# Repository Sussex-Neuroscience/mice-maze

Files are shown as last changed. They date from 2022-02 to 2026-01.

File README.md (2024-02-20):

# Mice maze
#### Active exploration setup for rodents

This is a repository for building and running an experiment investigating how sensory cues affect mouse exploration in a modifiable maze.

### List of repository contents ###

#### 3dmodels
* Models used to make/3dprint parts used in the maze setup.
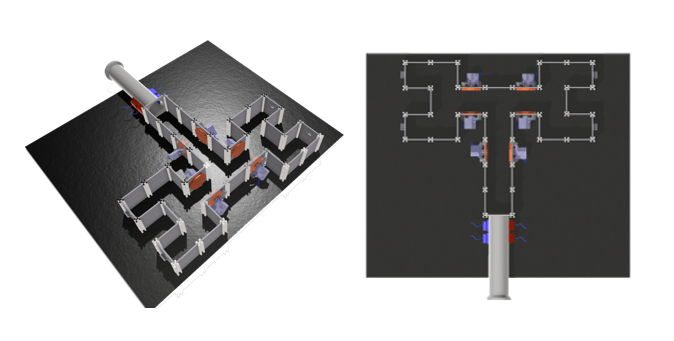
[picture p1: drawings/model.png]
alt text for screen readers tunnable walls


#### code
* Contains code used in the project.
* * Scripts used to process the video recordings of mice in the maze and a script used for the pilot deeplabcut test.
* * Arduino code to control stimuli settings and reward delivery.
* * Walkthrough to use the automatic maze.

#### construction_photos
* A selection of photos of the maze during it's development for illustrative purposes.

#### drawings
* Schematics and drawings. Such as the format of the base plate holes.

#### Contributors of the maze:
* Miguel Maravall
* Oluwaseyi Jesusanmi
* Andre Maia Chagas
* Yuri Elias Rodrigues
* Maja Nowak
* Marcus Burnell-Spector
* Shahd Al Balushi
* Isabel Maranhao
* Alejandra Carriero

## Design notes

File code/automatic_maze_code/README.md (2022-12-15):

## Automatic maze code

#### Entry sensor code using Beehive+micropython - **sensor.py**
* write on the terminal (Linux) when instructed
```
ampy --port /dev/ttyUSB0 --baud 115200 run path_to/sensor.py &> sensor.csv
```

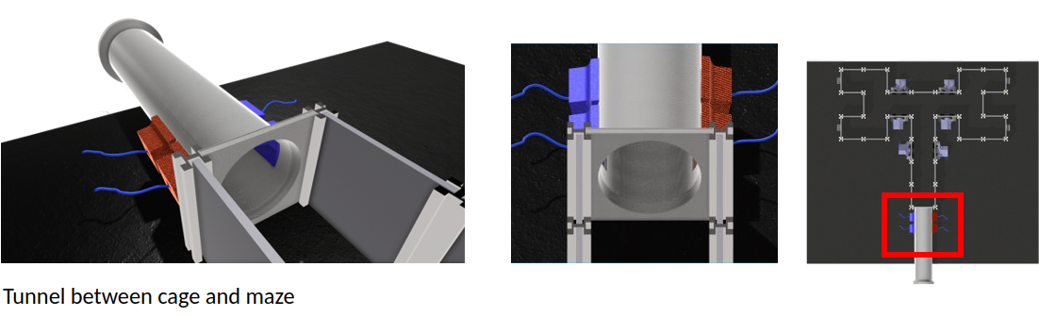
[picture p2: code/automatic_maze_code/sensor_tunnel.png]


#### Grated tunable walls code - *tunable_walls.py*
* First, upload a *standard firmata* ([tutorial how to upload standard firmata](https://www.instructables.com/Arduino-Installing-Standard-Firmata/)) to an Arduino Uno, and wire it using a breadboard.
* A calibration file needs to be created to interpolate the angles measured at 0°, 45°, 90° and 135°. A calibration example sheet is given at **angle_tuning.csv**.
* Once the servos are calibrated, the angles can be defined as the function *move_servo_tuned()* at *tunable_walls.py*. Example:
* * Move servo labelled "RR" to 90 using:
```
move_servo_tuned(90,"RR")
```

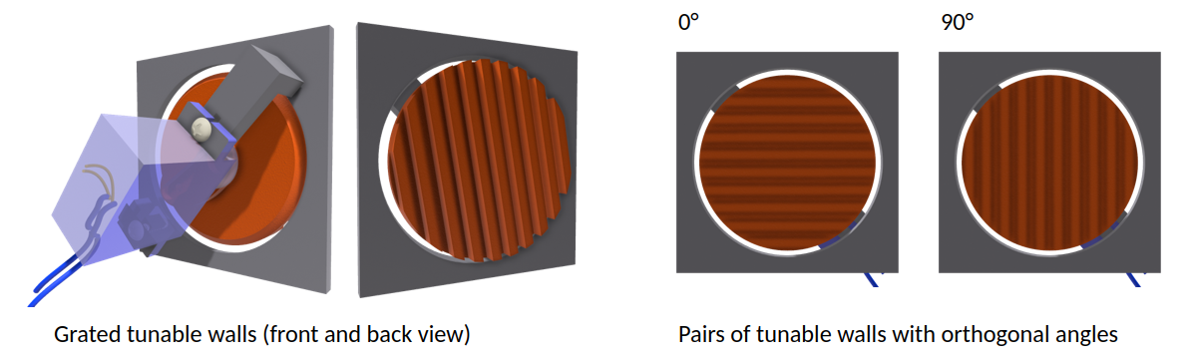
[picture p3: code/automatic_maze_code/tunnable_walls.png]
alt text for screen readers tunnable walls


#### Food delivery - *food_delivery.py*
* Food delivery is similar to the tunable walls code. First, upload *standard firmata* to an Arduino Uno and wire it using a breadboard.
* A calibration file also needs to be created to match the order in which the food pellet will be delivered and the necessary rotation. An example of the calibration is given at *food_tuning.csv*. The tunning can be found using the function *move_food_order()*. For example, a way to slowly deliver the reward:

```
for i in range(0,23,2):
      time.sleep(0.1)
      move_food_order(i,'LR')
```

#### Camera and position tracking for automated reward delivery - *automatic_maze_code_with_food.py*
* All operations on the camera are done using cv2-python. The detection of a correct trial is triggered using a pixel intensity threshold against a background recording done before the cage is placed. Note that the maze should not be shaken during this operation to displace the region of interest where the pixel intensity is measured.
* Sensor plotting is done in real-time using [PyQtGraph](https://www.pythonguis.com/tutorials/plotting-pyqtgraph/) for efficiency.
* Routines depending on the camera:
* * Pixel intensity averages for trial definition (hit/miss)
* * Position detection.
* * Time spent by the mouse in each region by trial and by session (*only implemented for the reward delivery place*).
* * Gimbal camera and focus feedback (*to be implemented*).
* * Distance/speed measures along the trial and session (*to be implemented*). This can be used to measure the engagement and how fast the mice finish the trial.
* * Tunable wall proximity measure (*to be implemented*). This would be useful to measure

#### GUI

#### Analysis code (to be implemented)
* Summary and update results to the last results
* Update a Markov model to predict exploration patterns using time spent on a region of interest covering the whole maze (online and offline).

#### Behavior task description on the automated maze (food version)
#### Behavior task description on the automated maze (liquid version)

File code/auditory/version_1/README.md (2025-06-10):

# Welcome to the Auditory part of the maze
## Hope you're here to stay!!

- The main logic of the experiment is in `main.py`. Feel free to modify it according to your needs. The code is designed to ask for user input but it is optimised to let you just hard code variables instead (it gets annoying to always input the same values for different mice, I get it. But if you work on more dynamic experiments, you have the option. All in all. The setup is designed to **give you options, nothing but options**.) 

- The trials generation is handled in `supfun_sequences.py`. 

- If you haven't calibrated your speaker yet, what are you waiting for? Head over to `speaker calibration scripts`. 
- If you don't need speaker calibration / have a better method (rude, but fine. At least share. How did you do it?), I recommend running `calibration_volume.py` to check which channel the sounds come out of.

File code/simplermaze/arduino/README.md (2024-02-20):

the code to run the servos requires an adafruit library as well as a serial communication parsing library. they can be found:

- https://github.com/adafruit/Adafruit-PWM-Servo-Driver-Library
- https://github.com/kroimon/Arduino-SerialCommand

more info on how to use the adafruit library here: 
https://learn.adafruit.com/16-channel-pwm-servo-driver/using-the-adafruit-library

Serial commands are structured in the following way:

- to change the orientation of a grating, the command going to the arduino board should be a string with the keyword "grating", followed by the coded location of the grating and the angle the grating needs to be moved to. Example: "gratingLL 180"

- to send commands for rewards to be dispensed, the command going to the arduino board should be a string with the keyword "reward", folllowed by the location where the reward is to be given. Example: "rewardA"

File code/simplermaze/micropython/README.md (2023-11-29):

## code to run the PCA9685 on micropython

this leverages the Adafruit library which is currently not being actively developed.

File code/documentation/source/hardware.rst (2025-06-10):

Hardware Documentation
======================

Materials List
--------------

General Materials
-----------------
- **Panels and Baseplate**:
  - 50 side panels: Black, 50 × 50 × 3 mm.
  - 1 baseplate: 10 mm thickness, 700 × 700 mm, black infrared-transmitting (Code: 962).
- **Maker Beams for Structural Support**:
  - XL beams (50 mm length, black anodized aluminum).
  - **Bolts for Maker Beams:** M3 bolts (16 mm), M3 nuts (1 per bolt).
- **Bolts for Feet:** M6 bolts and nuts for stabilization (1 per corner).
- **Legs:**
  - Dimensions: 50.8 × 50.8 × 1.6 mm.
  - Length: 880 mm; horizontal bars: 660 mm.
  - Accessories: 4 plastic joints and bottoms.

Construction Instructions
-------------------------

Base Assembly
~~~~~~~~~~~~~
1. Attach the maker beams to the baseplate using M3 bolts and nuts.
2. Ensure a stable connection by tightening each bolt securely.

Legs and Stabilization
~~~~~~~~~~~~~~~~~~~~~~
1. Secure the legs to the baseplate using M6 bolts and nuts.
2. Add plastic joints and bottoms for stability.
3. Verify the assembly is level to prevent wobbling.

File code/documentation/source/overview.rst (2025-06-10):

Overview
========

The Mice-Maze project provides a modular system for researchers to investigate rodent exploration behavior and sensory cue processing. The maze's flexible design includes interchangeable components and precise control of environmental stimuli. This documentation details the hardware and software requirements, assembly instructions, and usage guidelines.

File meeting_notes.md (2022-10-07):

### Meetings:

#### 19/01/2022 Seyi & Andre
Figuring out initial bill of materials and acrylic dimensions:

- considerting the use of makerbeams (plates will slide in them), we need acrylic plates that are a bit longer than the area the mouse will have access to.

All side/wall plates will have the same dimensions and there will be a base plate and a ceiling plate.

on the base plate we will have regularly spaced threads, so that makerbeam posts can be fixed in. and different maze styles can be built.

- base plate: (paper dimensions - 12.7mm thickness 609.6 X 609.6 mm) for our system: 600 X 600 X 12 mm
- side plate: (paper dimensions - 40.63 X 50.8 X 3.175 mm) For our system: 50 X 50 X 3 mm 
- maker beams XL for support: 50mm length, black anodised aluminium.
- M3 bolts to fix the makerbeams on the plates
- m6 bolts as feet for the floor plate

local company for acrylic: https://www.brightonandhoveplastics.co.uk/index.php/products-acrylic_sheet/?k=23991:5::
makerbeam shop https://www.makerbeam.com/makerbeamxl/makerbeamxl-15x15mm-profile-lengths-anodised-in-bl/
screwfix for bolts https://www.screwfix.com/p/easyfix-bright-zinc-plated-pan-head-machine-screws-m3-x-20mm-25-pack/5875j?cm_sp=managedredirect-_-screwsfixings-_-m3bolts&_requestid=183859

We decided to go for an 4 arm maze initially to test things.

There are 8 end points in this. 

To build this, we need (with spares) 50 side panels and 50 makerbeam posts, celing and floor plates.
Also need M3 bolts

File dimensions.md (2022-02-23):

***Converted/ extracted dimensions of Rosenberg Maze***

Whole maze dimensions Length: 609.6mm, Width: 609.6mm, Height (ie Floor to ceiling): 50.8mm

Ceiling thickness: 12.7mm
Acrylic wall thickness: 3.175mm

Corridor width: 28.575mm

In their design. From the top of the maze to the bottom there are 15 panels. 609.5/15=40.63

Therefore each panel width is 40.63mm

To the first junction (the first T) there are 7 panels. So the first corridor is 284.41mm.

Turning into the arms of the T there are 3 panels on each side, meaning an arm length of 121.89

***Measurements for our project maze***

Makerbeams: Height and width of 10mm. Variable length. They will be above and below the acrylic wall.

Acrylic wall height: 30.79mm  
Acrylic wall panel length: 40mm  
Acrylic wall panel thickness: Dependent on makerbeam T-slot.

Maker beams have optional lengths of 40mm premade, which is close to thee 40.63mm panels of the Rosenberg made, so we can alter the panel width to suit this.

To form a T-maze only, these are the number of parts needed.  
Number of panels needed: 29  
Number of (40mm) makerbeams needed: 58

***Final part measurements used during construction***

*A few measurements to be reconfirmed with tool*

Acrylic wall panels: H-50mm, L-50mm, W/Thicness - Xmm   

Screws: M3 16mm, with an M3 nut used on the underside of the maze baseplate.

Baseplate Thickness: 10mm (Smaller thicknesses of ~7.5mm up would also work.
Baseplate is 700mm by 700mm.

Makerbeams: [10 x 10 makerbeams](https://www.makerbeam.com/makerbeam/makerbeam-10x10mm-profile-lengths-anodised-in-blac/) were used with a custom length of 50mm.

Infra-red camera used is found at [this link](https://www.amazon.co.uk/ELP-Webcam-Windows-machine-ELP-USBFHD05MT-RL36-U/dp/B015VE6MII/ref=sr_1_1_sspa?crid=1YP1F3UZ7P0DA&keywords=elp+infrared+camera&qid=1643305666&sprefix=elp+infrared+camera%2Caps%2C273&sr=8-1-spons&psc=1&spLa=ZW5jcnlwdGVkUXVhbGlmaWVyPUEyVTRNUFhHNFo2VUYwJmVuY3J5cHRlZElkPUEwNzY4NTUyMTJWRjROS0NGMTdWSiZlbmNyeXB0ZWRBZElkPUEwMjA0ODUwMkg1SVhWTzJMSVlXUyZ3aWRnZXROYW1lPXNwX2F0ZiZhY3Rpb249Y2xpY2tSZWRpcmVjdCZkb05vdExvZ0NsaWNrPXRydWU=), and the infra-red illuminator is a [this link](https://www.amazon.co.uk/dp/B01N76QRHV/ref=sspa_dk_detail_1?psc=1&pd_rd_i=B01N76QRHV&pd_rd_w=BuWW7&pf_rd_p=c899a50b-8835-46b4-89a0-fdf052ea9b60&pd_rd_wg=3Z9Ro&pf_rd_r=JVWXG686S572C72FK036&pd_rd_r=87af8edc-d196-40cb-8f1a-5166b4e7a4cc&spLa=ZW5jcnlwdGVkUXVhbGlmaWVyPUEyV1JNU0FENUtYVzZVJmVuY3J5cHRlZElkPUEwNDI2ODEyRFlDRFlOTjgwSEJYJmVuY3J5cHRlZEFkSWQ9QTA2MTg4OTc0MFcySUoxOUw3OVkmd2lkZ2V0TmFtZT1zcF9kZXRhaWwmYWN0aW9uPWNsaWNrUmVkaXJlY3QmZG9Ob3RMb2dDbGljaz10cnVl)

We will use [these beams](https://www.metals4u.co.uk/materials/aluminium/aluminium-box-section/799-p?vat=inc&gcl[…]yC8SSxSnme3ri-O_1YQuGo-yPlagg_-HQaAv4HEALw_wcB&gclsrc=aw.ds) for the frame, with velcro on the maze baseplate and and on the beams for easy removal.
The beams fit together with plastic joints, and from the end of a joint to where the bar fits to the joint is 40mm.
We will 4 metal bars of 620mm each to go around the outside of the maze. And 4 bars of 760mm each to be the legs of the maze.

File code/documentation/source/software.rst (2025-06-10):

Software Documentation
======================

Code Overview
-------------
- The repository includes:
  - Scripts for video processing and analysis.
  - Code to control maze stimuli and motor functions.

Running the Software
--------------------
1. Launch the Python script to initialize the experiment.
2. Adjust camera settings and stimuli parameters as needed.
3. Begin the experiment and monitor data collection.

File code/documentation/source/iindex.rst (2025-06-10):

.. Mice maze documentation master file, created by
   sphinx-quickstart on Thu Oct 10 16:22:44 2024.
   You can adapt this file completely to your liking, but it should at least
   contain the root `toctree` directive.

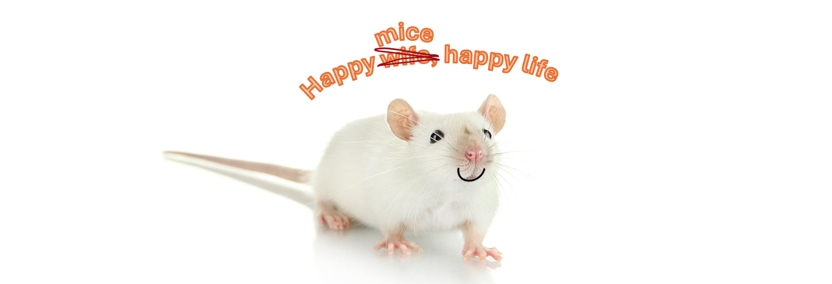
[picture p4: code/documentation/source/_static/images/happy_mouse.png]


the aMAZEing maze documentation
=======================

**Active exploration setup for rodents**
This is a repository for building and running an experiment investigating how sensory cues affect mouse exploration in a modifiable maze.

Check out the :doc:`usage` section for further information, including how to :ref:`install <getting_started>` the project.

Welcome to Mice-Maze Documentation!
====================================

.. toctree::
   :maxdepth: 2
   :caption: Contents

   overview
   getting_started
   hardware
   software
   usage
   examples
   troubleshooting
   references

Indices and tables
==================
* :ref:`genindex`
* :ref:`modindex`
* :ref:`search`

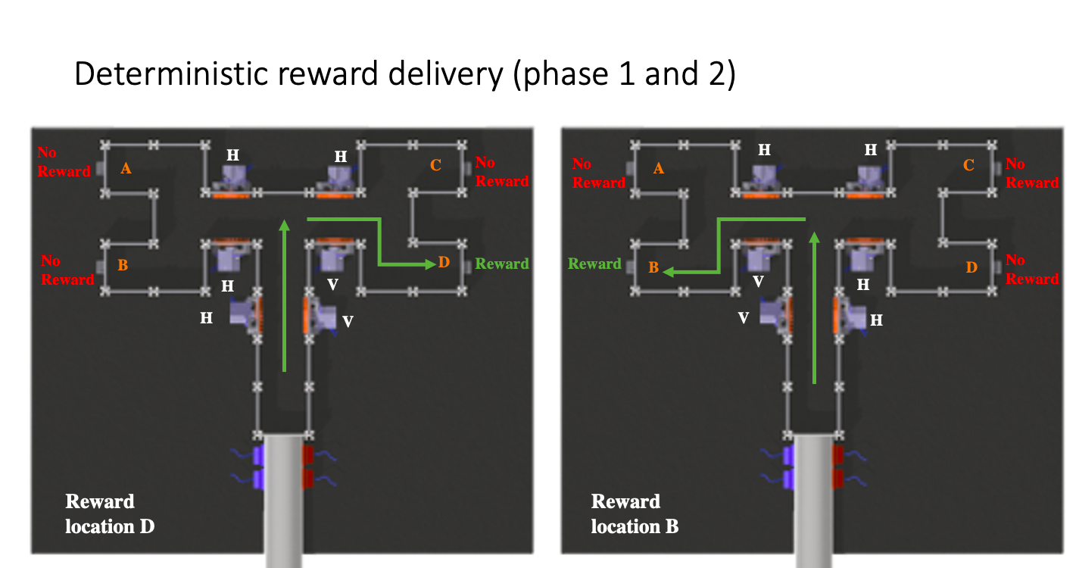
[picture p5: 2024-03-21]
drawings/task_design_2.png

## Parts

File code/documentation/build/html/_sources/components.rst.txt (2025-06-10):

Build the maze
==================

Maze structure
_______________

To build this, we need (with spares):

- **50 side panels and 50 maker beam posts, and floor plate. Also need M3 bolts, legs and camera**

- **Colour for baseplate and panels:** Colour: Black Code: 962, Dimensions(mm): 3050 x 2030, Thickness (mm): 3 – 15, Light Transmission (%): 0 Infrared Transmitting Side panels: 50 X 50 X 3 mm Baseplate: Thickness is 10mm, size 700mm by 700mm Maker beams: maker beams XL for support: 50mm length, black anodised aluminium.

- **Bolts for maker beams:** M3 bolts to fix the maker beams on the plates (M3 16mm, with an M3 nut used on the underside of the maze baseplate.) (1bolt and 1 nut per Maker beam) (bolts and nuts can be bought from screwfix?)

- **Bolts for feet:** M6 bolts as feet for the floor plate – Bolts not attached to the legs, it is to prevent the top falling off. One nut of top side and one a bottom side, with one bolt per corner. (bolts and nuts can be bought from screwfix?) Legs: 50.8mm x 50.8mm x 1.6mm, with Legs length 880mm, the bars that go round are 660 mm, 4 plastic joints and 4 plastic bottoms for the feet

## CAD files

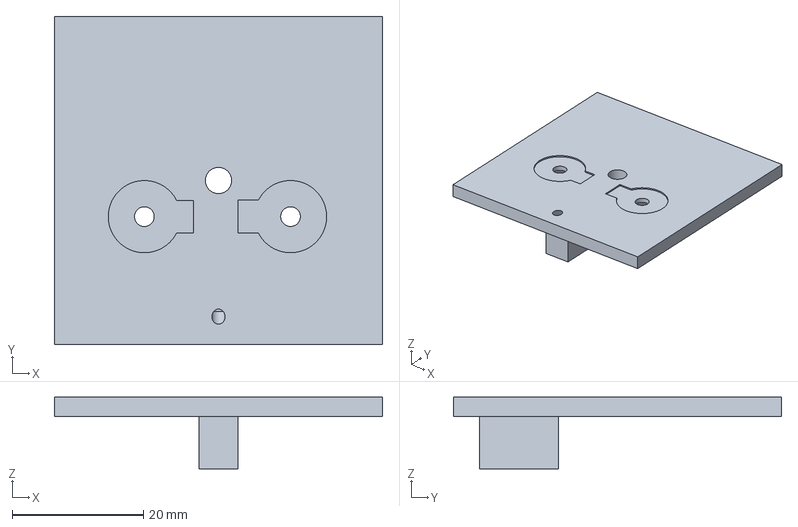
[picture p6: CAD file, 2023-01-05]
3dmodels/maze_parts/spout/spout_holder-main_plate.amf
50.0 x 50.0 x 10.9 mm

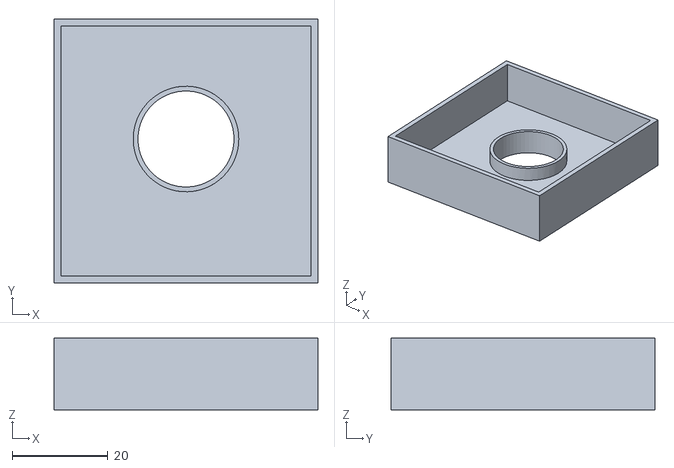
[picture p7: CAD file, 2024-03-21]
3dmodels/camera_holder/camera_lid_v1.stl
55.0 x 55.0 x 15.0

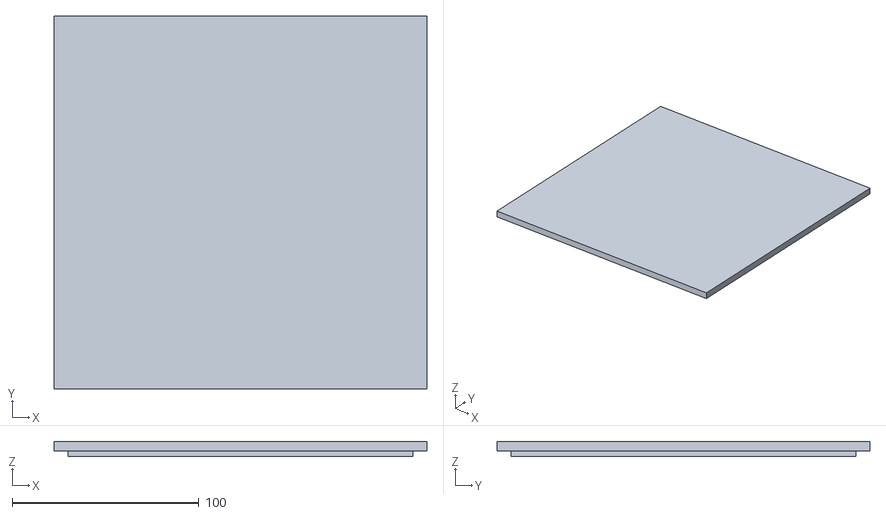
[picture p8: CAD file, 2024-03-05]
3dmodels/electronics_enclosure_lid_v2.stl
200.0 x 200.0 x 8.00

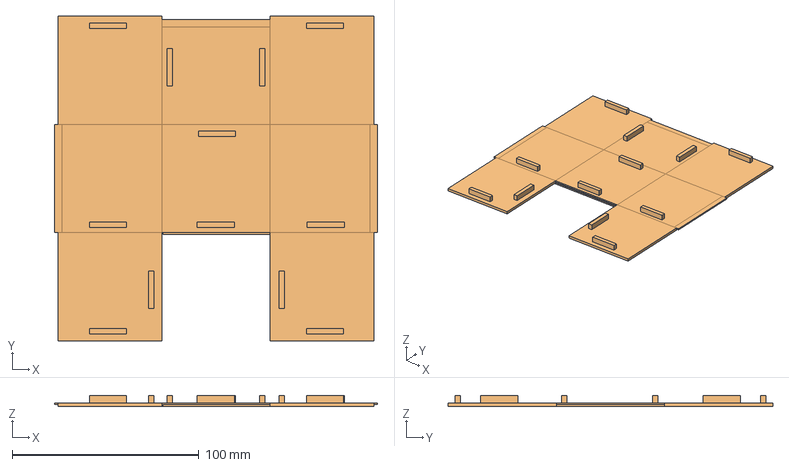
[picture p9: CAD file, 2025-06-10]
3dmodels/maze_parts/maze_cover/maze_cover_B_v4.FCStd
173.0 x 174.0 x 6.00 mm

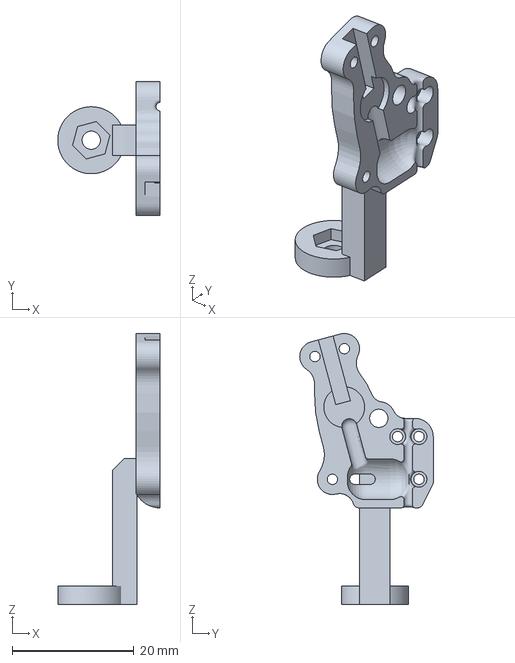
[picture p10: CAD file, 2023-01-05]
3dmodels/maze_parts/spout/spout_holder-holder_left.amf
16.8 x 21.9 x 44.5 mm

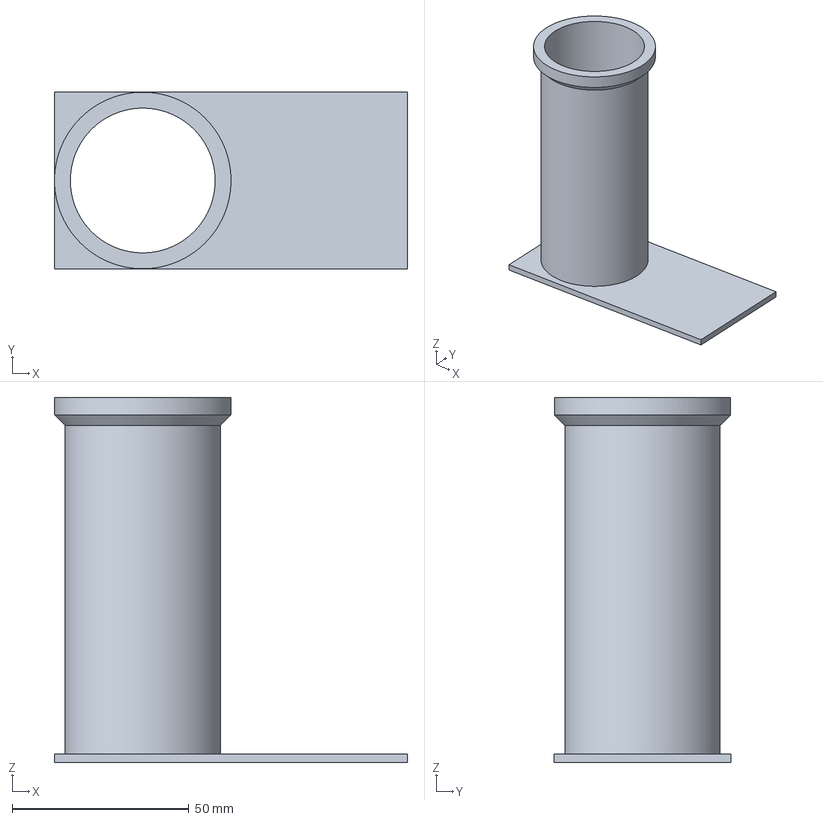
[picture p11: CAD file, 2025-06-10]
3dmodels/maze_parts/tunnel/Maze2_transfer_tunnel_higher.walls.3mf
100.0 x 50.0 x 103.5 mm

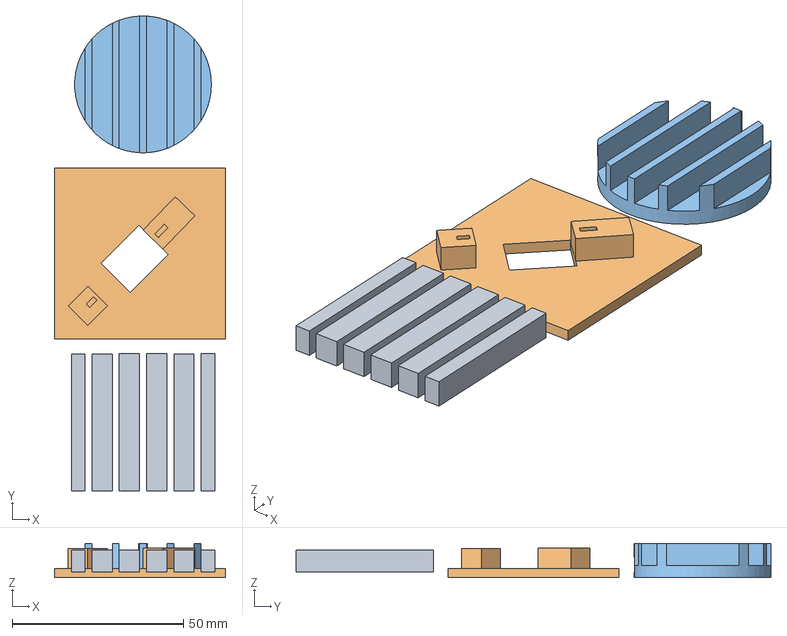
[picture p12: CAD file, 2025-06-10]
3dmodels/moveable_wall/cog calibration/new_wall_maze_v15.FCStd
50.0 x 138.9 x 10.0 mm

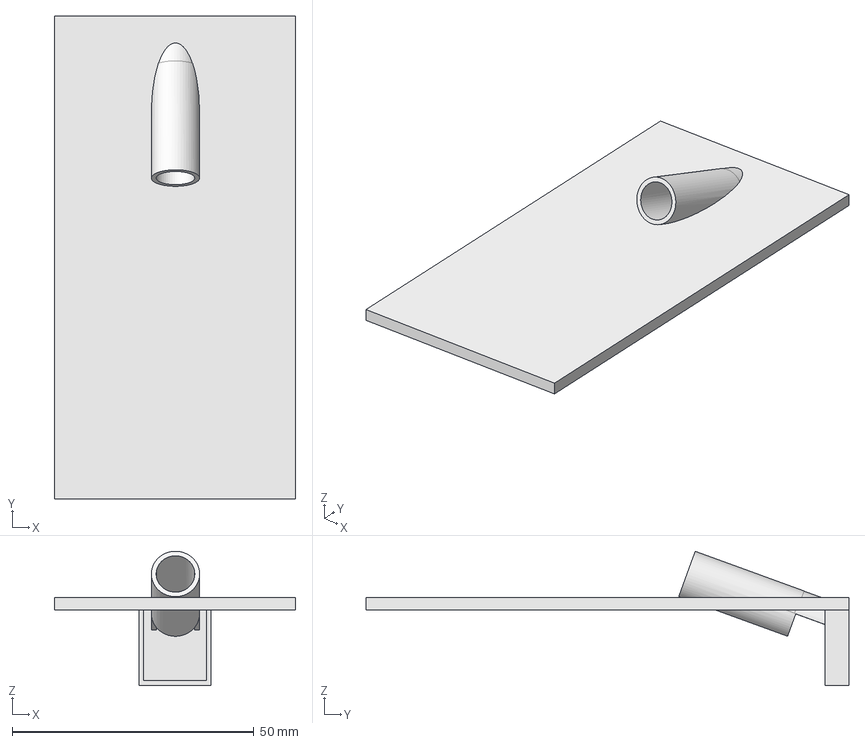
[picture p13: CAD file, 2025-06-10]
3dmodels/reward delivery/reward_chute_Wall_v4.FCStd
50.0 x 100.0 x 27.8 mm

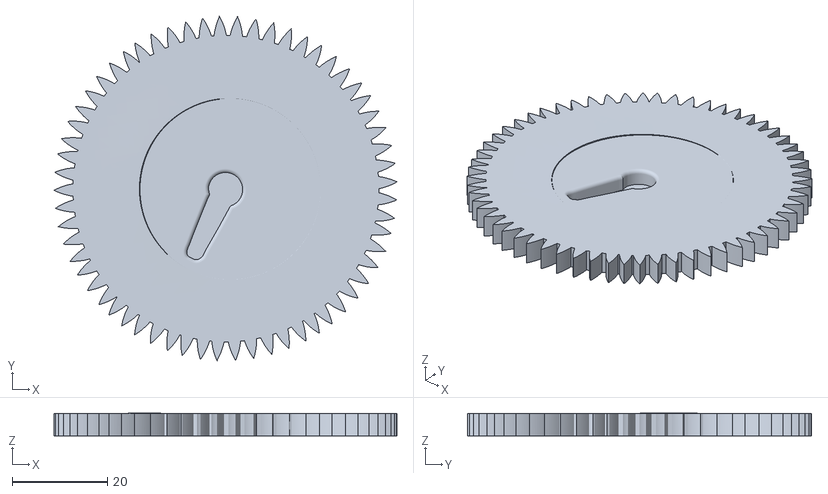
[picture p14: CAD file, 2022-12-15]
3dmodels/solid_reward_tray/cog.stl
72.1 x 72.3 x 4.78

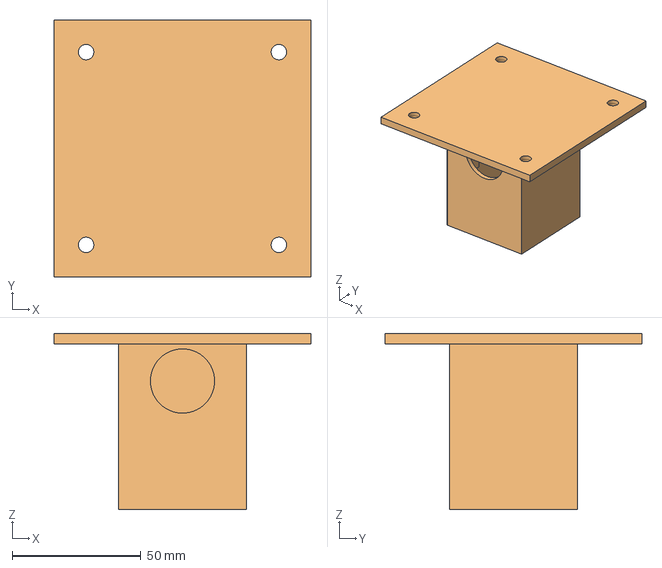
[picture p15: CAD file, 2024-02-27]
3dmodels/camera_holder/camera_box_v3.FCStd
100.0 x 100.0 x 68.5 mm

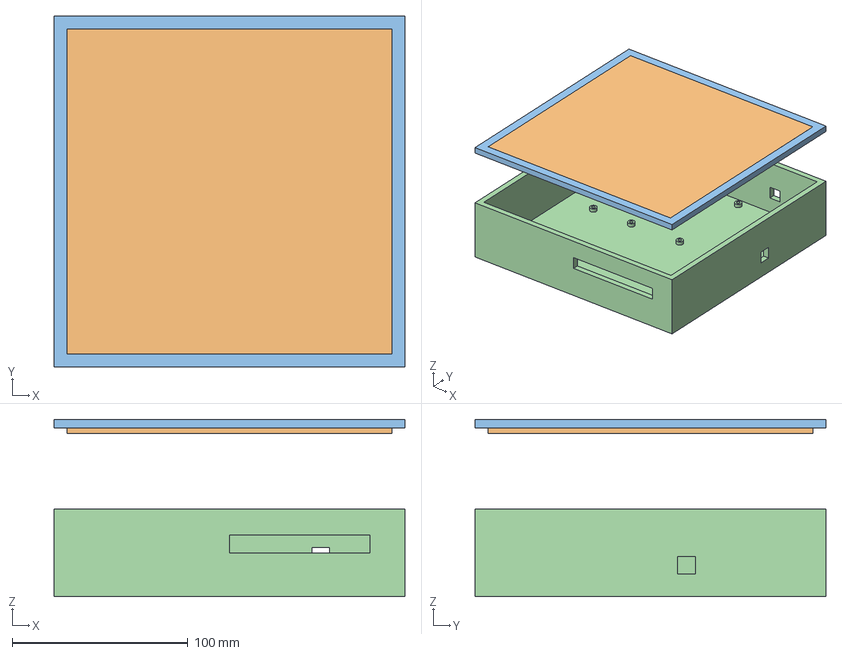
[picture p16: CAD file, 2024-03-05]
3dmodels/electronics_enclosure_v2.FCStd
200.0 x 200.0 x 101.0 mm
lid

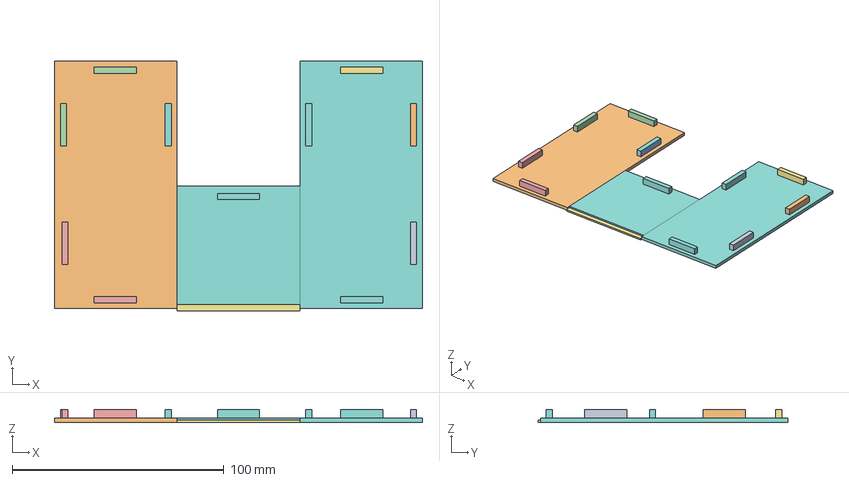
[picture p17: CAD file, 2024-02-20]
3dmodels/maze_parts/maze_cover/maze_cover_C_v3.FCStd
174.0 x 118.0 x 6.00 mm

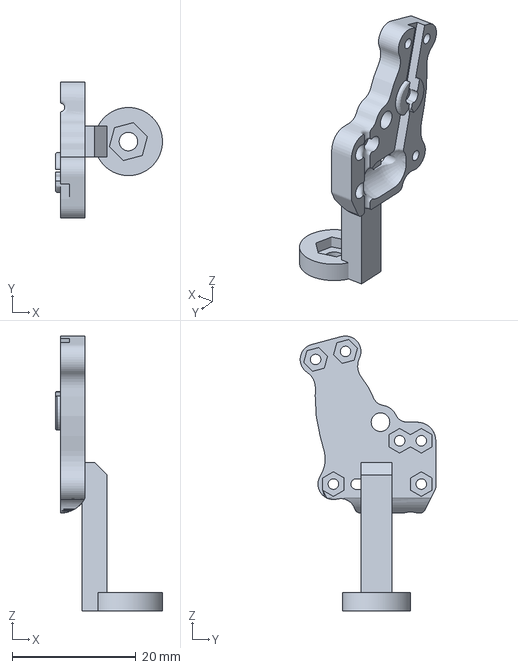
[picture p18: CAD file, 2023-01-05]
3dmodels/maze_parts/spout/spout_holder-holder_right.amf
17.3 x 21.9 x 44.4 mm

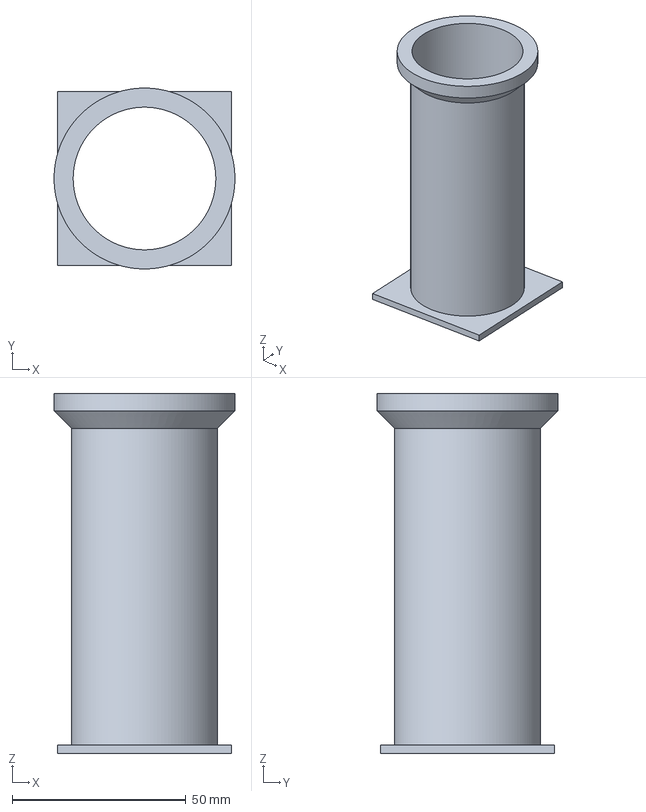
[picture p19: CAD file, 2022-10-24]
3dmodels/maze_parts/tunnel/transfer_tunnel-Cut.amf
52.0 x 52.0 x 103.5 mm

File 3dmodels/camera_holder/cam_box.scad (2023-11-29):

//cable hole diameter
cb_diameter = 20;

//base of camera board to top of lens
cam_h = 25;

//height camera should be suspended above the bottom of the box
cam_suspend_h = 30;

//side length of square indents the camera board will rest on
rest_indent_l = 7;

//whole camera board length. It is square
cam_board_l = 39;

//wall thickness of box x2
wall_thick = 6;

//length of box
box_l = cam_board_l+wall_thick;


//base square length
base_l = 70;

//added distance to get to middle of base square
base_add = (base_l-(cam_board_l+wall_thick))/2;

//subract cylinder from box with subracted box
translate([base_add, base_add, wall_thick])
{
difference()
{
// make cube which will be subtracted from bigger cube
difference()
{
{cube([cam_board_l+wall_thick, cam_board_l+wall_thick, cam_suspend_h+cam_h+wall_thick]);

translate([wall_thick/2, wall_thick/2, wall_thick/2])
{cube([cam_board_l, cam_board_l, cam_suspend_h+cam_h+5]);}

}}
// check how to rotate a cylinder

//make cylinder
//rotate by degrees around a defined axis

//define where to put hole
translate([box_l/2,box_l+1,20])
{rotate([90,0,0])
{cylinder(h=wall_thick/2+2, r1 = cb_diameter/2, r2 = cb_diameter/2);
}}}}


//change circularity of cylinder
$fn = 30;

//add indents for camera to rest on

// define thickness of the indent
indent_h = cam_suspend_h;

//module for supporting pillars
module pillar(){
    cube([rest_indent_l, rest_indent_l, indent_h]);
}

//module for m3 screw holes with a 0.1mm tolerance
module m3_hole(){
    diameter=3;
    tol = 0.1;
    cylinder(h=wall_thick*2, d1 = 
    diameter+tol*2, d2 = diameter+tol*2);
}

translate([base_add, base_add, wall_thick])
{
//make indent cube and move it to the corners of the box
translate([wall_thick/2,wall_thick/2,wall_thick/2])   
{difference(){
pillar();
 translate([rest_indent_l/2, rest_indent_l/2, cam_suspend_h-wall_thick*2+1]){    
 m3_hole();}}
}

//indent 2
translate([cam_board_l-wall_thick/1.5,wall_thick/2,wall_thick/2])
{difference(){
pillar();
 translate([rest_indent_l/2, rest_indent_l/2, cam_suspend_h-wall_thick*2+1]){    
 m3_hole();}}
}

//indent 3
translate([cam_board_l-wall_thick/1.5,cam_board_l-wall_thick/1.5,wall_thick/2])
{difference(){
pillar();
 translate([rest_indent_l/2, rest_indent_l/2, cam_suspend_h-wall_thick*2+1]){    
 m3_hole();}}
}

//indent 4
translate([wall_thick/2,cam_board_l-wall_thick/1.5,wall_thick/2])
{difference(){
pillar();
 translate([rest_indent_l/2, rest_indent_l/2, cam_suspend_h-wall_thick*2+1]){    
 m3_hole();}}
}
}

//how far in m3 holes should be
m3_loc = 5;

//make base plate and drill holes
difference()
{
cube([base_l, base_l, wall_thick]);
    
 translate([m3_loc, m3_loc, -1]){
 m3_hole();}

 translate([base_l-m3_loc, base_l-m3_loc,-1]){
 m3_hole();}

 translate([base_l-m3_loc, m3_loc,-1]){
 m3_hole();}

 translate([m3_loc, base_l-m3_loc, -1]){
 m3_hole();}
} 

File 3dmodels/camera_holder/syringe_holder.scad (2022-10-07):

//length of cross section in makerbeam
mb_inner_w = 5.7;
//width of entrance to cross of maker beam
mb_ent_w = 3;
//depth of cross section in maker beam
mb_cross_d =2.5;

//start with rectangle for inner width
cube([mb_inner_w, mb_cross_d, 20]);

//ok now need rectangle coming out out the maker beam, but need to translate it
translate([(mb_inner_w-mb_ent_w)/2,mb_cross_d,8])
{cube([mb_ent_w, 1.5, 8]);
}

//next need empty circle/cylinder that will hold the test tube as a snug fit
//need to translate it to beyond the second cylinder as well
difference(){
translate([mb_inner_w/2,mb_cross_d+1.2+16.5/2,10])
{cylinder(h=3, d1=16.7, d2=17, center = false);
}
translate([mb_inner_w/2,mb_cross_d+1.2+16.5/2,10])
{cylinder(h=6, d1=16.4, d2=16, cantre=false);}
}

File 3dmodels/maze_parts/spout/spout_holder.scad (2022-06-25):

platex = 50;
platey = 50;
platez = 3;

spoutHD = 2;

//tolerance
tol = 0.1;


module container(){
    difference(){
    cube([6,10,20]);
    
    translate([1,-2,1]){
        cube([4,10,20]);
        }//end translate
    }//end difference
    
}//end module
    
//difference(){
union(){
cube([platex,platey,platez]);

    translate([platex/2-3,2,0]){
    rotate([-90,0,0]){
    container();
    }//end rotate
}//end translate
}//end union


translate([platex/2,platey/2,-1]){
    cylinder(d=spoutHD,h=3*platez);
    
    }//end translate

translate([platex/2,5,-1]){
    rotate([30,0,0])
    cylinder(d=spoutHD,h=3*platez);
    
    }//end translate


//}

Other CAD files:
3dmodels/moveable_wall/new_wall_maze_v13.FCStd
3dmodels/moveable_wall/cog calibration/new_wall_maze_v14.FCStd
3dmodels/moveable_wall/new_wall_maze_v11.FCStd
3dmodels/reward delivery/reward_chute_Wall_v3.FCStd
3dmodels/archive/electronics_enclosure.FCStd
3dmodels/archive/electronics_enclosure/enclosure.FCStd
3dmodels/archive/gratings/gratings.scad
3dmodels/archive/gratings/gratings.stl
3dmodels/archive/habituation_sink/habituation_sink.3mf
3dmodels/archive/habituation_sink/habituation_sink.stl
3dmodels/archive/moveable_wall.3mf
3dmodels/archive/moveable_wall.stl
3dmodels/archive/new_wall_maze.FCStd
3dmodels/archive/new_wall_maze_cog_v4.stl
3dmodels/archive/new_wall_maze_cog_v6.FCStd
3dmodels/archive/new_wall_maze_cog_v6.stl
3dmodels/archive/new_wall_maze_cog_v7.FCStd
3dmodels/archive/new_wall_maze_cog_v7_test.FCStd
3dmodels/archive/new_wall_maze_cog_v7_test.stl
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

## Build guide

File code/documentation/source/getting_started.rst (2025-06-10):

.. _getting_started:

Getting Started
===============

Prerequisites
-------------
1. **Hardware**:
   - A PC with sufficient processing power for video analysis and Arduino control.
   - Required components (detailed in the Hardware Documentation section).
2. **Software**:
   - Python (minimum version: 3.8).
   - Arduino IDE for programming hardware controllers.
   - Git for accessing the repository.

Installation Instructions
--------------------------
1. Clone the repository:
   ```bash
   git clone https://github.com/Sussex-Neuroscience/mice-maze.git
   ```
2. Install required Python libraries:
   ```bash
   pip install -r requirements.txt
   ```
3. Set up Arduino libraries and upload the necessary sketches to the Arduino.
4. Install the camera driver (if needed).

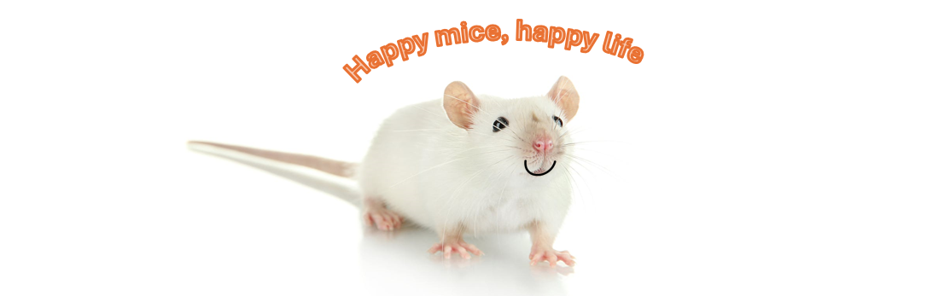
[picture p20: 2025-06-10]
code/documentation/build/html/_static/images/mouse_ban.png

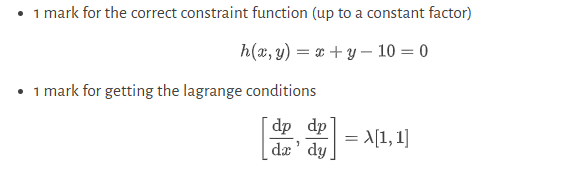
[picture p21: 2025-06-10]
code/documentation/build/html/_static/images/Screenshot 2025-01-23 184648.png

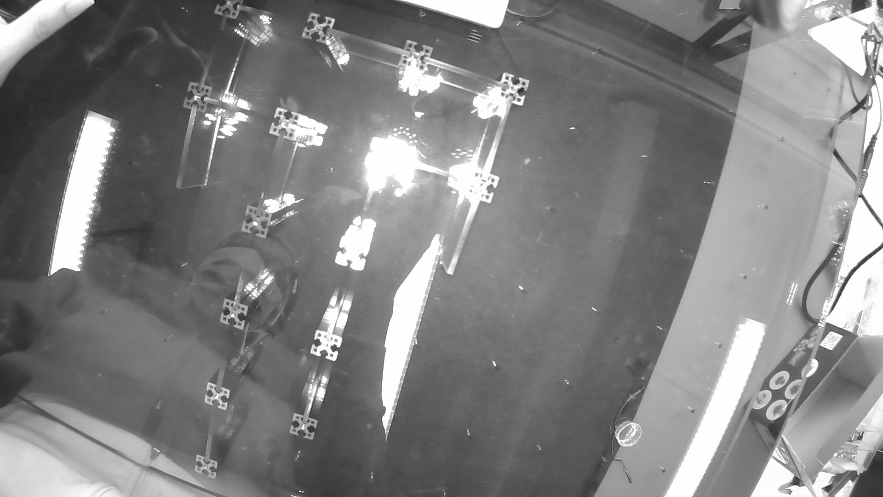
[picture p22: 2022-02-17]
construction_photos/topplate_view_infrared1.jpg

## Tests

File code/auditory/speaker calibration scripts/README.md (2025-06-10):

This directory includes the scripts you need to calibrate your speaker, if it also has a non-flat frequency response. 

We tried 2 approaches: 
1. The approach that we ended up using is in the second half of notebook_calibration.ipynb. We retrieved the datapoints for the speaker frequency response using an online tool called WebPlotDigitizer (https://automeris.io/), and computed the gain to flatten the frequency response. Obviously make sure to replace the path to the .csv file with the path to your .csv file. Unless you are also using the Avisoft Vifa Ultrasonic speaker. 
2. The approach we tried and tested so you don't have to is: generate sounds by running calibration_freq.py and record them with an ultrasonic microphone and a digital sound meter, found a calibration constant to map FFT amplitude of the frequency to a volume in dB SPL. Ensure to change the sample rate of the output to the sample rate used by the sound card. Make sure to have a look at fft_volume and notebook_calibration.ipynb to modify according to your data/sound recording.

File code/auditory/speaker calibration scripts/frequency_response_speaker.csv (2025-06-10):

Frequency_kHz | Attenuation_dB
5.485163526 | -2.105263158
9.20781893 | 0
10.28806584 | 0
15.01335644 | -6.736842105
15.62612808 | -7.263157895
19.83160061 | -2.736842105
21.38293264 | -1.789473684
24.15980796 | -1.894736842
30.17561909 | -2.210526316
35.13193993 | -0.105263158
37.58844127 | -1.578947368
40.04043029 | -3.578947368
43.11331312 | -5.157894737
45.42903039 | -5.052631579
49.46574255 | -2.210526316
51.16146849 | -2.421052632
54.21269222 | -6.526315789
55.28842683 | -7.052631579
59.7962241 | -3.263157895

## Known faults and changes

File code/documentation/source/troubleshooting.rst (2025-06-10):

Troubleshooting
===============

Common Issues
-------------

1. **Camera not detected**:
   - Check USB connections and reinstall drivers if necessary.
2. **Motors not responding**:
   - Verify Arduino connections and ensure the correct sketch is uploaded.

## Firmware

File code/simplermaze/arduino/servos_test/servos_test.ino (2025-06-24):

#include <SerialCommand.h>
#include <Wire.h>
#include <Adafruit_PWMServoDriver.h>

// called this way, it uses the default address 0x40
//Adafruit_PWMServoDriver pwm = Adafruit_PWMServoDriver();
// you can also call it with a different address you want
//Adafruit_PWMServoDriver pwm = Adafruit_PWMServoDriver(0x41);
// you can also call it with a different address and I2C interface

Adafruit_PWMServoDriver pwm = Adafruit_PWMServoDriver(0x40, Wire);

int servoNum = 100;

// Depending on your servo make, the pulse width min and max may vary, you 
// want these to be as small/large as possible without hitting the hard stop
// for max range. You'll have to tweak them as necessary to match the servos you
// have!
#define SERVOMIN  150 // This is the 'minimum' pulse length count (out of 4096)
#define SERVOMAX  600 // This is the 'maximum' pulse length count (out of 4096)
#define USMIN  600 // This is the rounded 'minimum' microsecond length based on the minimum pulse of 150
#define USMAX  2400 // This is the rounded 'maximum' microsecond length based on the maximum pulse of 600

#define SERVO_FREQ 50 // Analog servos run at ~50 Hz updates

#define REWSERVOMIN  190 // This is the 'minimum' pulse length count (out of 4096)
#define REWSERVOMAX  560 // This is the 'maximum' pulse length count (out of 4096)
#define REWUSMIN  750 // This is the rounded 'minimum' microsecond length based on the minimum pulse of 150
#define REWUSMAX  2250 // This is the rounded 'maximum' microsecond length based on the maximum pulse of 600


#define GRATSERVOMIN  225 // This is the 'minimum' pulse length count (out of 4096) for the https://www.pololu.com/file/0J1435/FS90-specs.pdf
#define GRATSERVOMAX  525 // This is the 'maximum' pulse length count (out of 4096) for the https://www.pololu.com/file/0J1435/FS90-specs.pdf
#define GRATSERVOUSMIN 900 // for the https://www.pololu.com/file/0J1435/FS90-specs.pdf
#define GRATSERVOUSMAX 2100 // for the https://www.pololu.com/file/0J1435/FS90-specs.pdf

// our servo # counter
//uint8_t servoNum = 0;

#define gratingLnum 0
#define gratingRnum 1
#define gratingLRnum 2
#define gratingRLnum 3
#define gratingLLnum 4
#define gratingRRnum 5

//reward location A
#define IRsensorA 2
#define rewardMotorA 8
//reward location B
#define IRsensorB 15
#define rewardMotorB 9
//reward location C
#define IRsensorC 17
#define rewardMotorC 7
//reward location D
#define IRsensorD 16
#define rewardMotorD 6

int max_degree =180;

//int servoNum = 0;
int rewardServoMovTime = 400;
int IRsensor = 0;
int degree = 0;
int IRvalue = 0;
int time1 = 0;
int time2 = 0;
int pulseLen = 0;
int pelletDropped = 0;
int rewPulseLen1 = map(90, 0, 180, REWSERVOMIN, REWSERVOMAX);
int rewPulseLen2 = map(45, 0, 180, REWSERVOMIN, REWSERVOMAX);

//SerialCommand sCmd;     // The demo SerialCommand object


void setup() {
  Serial.begin(115200);

  //Wire.begin(14, 27);
  //Wire.begin(5, 18);
  pinMode(IRsensorA,INPUT);
  pinMode(IRsensorB,INPUT);
  pinMode(IRsensorC,INPUT);
  pinMode(IRsensorD,INPUT);



  

  
  // generic functions for development/understanding the parsing library
  //sCmd.addCommand("HELLO", sayHello);        // Echos the string argument back
  //sCmd.addCommand("P",     processCommand);  // Converts two arguments to integers and echos them back
  //sCmd.setDefaultHandler(unrecognized);      // Handler for command that isn't matched  (says "What?")


  //servo library initialization
  pwm.begin();
  /*
   * In theory the internal oscillator (clock) is 25MHz but it really isn't
   * that precise. You can 'calibrate' this by tweaking this number until
   * you get the PWM update frequency you're expecting!
   * The int.osc. for the PCA9685 chip is a range between about 23-27MHz and
   * is used for calculating things like writeMicroseconds()
   * Analog servos run at ~50 Hz updates, It is importaint to use an
   * oscilloscope in setting the int.osc frequency for the I2C PCA9685 chip.
   * 1) Attach the oscilloscope to one of the PWM signal pins and ground on
   *    the I2C PCA9685 chip you are setting the value for.
   * 2) Adjust setOscillatorFrequency() until the PWM update frequency is the
   *    expected value (50Hz for most ESCs)
   * Setting the value here is specific to each individual I2C PCA9685 chip and
   * affects the calculations for the PWM update frequency. 
   * Failure to correctly set the int.osc value will cause unexpected PWM results
   */
  pwm.setOscillatorFrequency(27000000);
  pwm.setPWMFreq(SERVO_FREQ);  // Analog servos run at ~50 Hz updates

  delay(10);

}// setup

void loop() {
  //Serial.println("aqui");
  for (int i=0;i<10;i++ ){
    for (int servo_num=0;servo_num<10;servo_num++){
      Serial.println(servo_num);
      for (int atempts=0;atempts<5;atempts++){
        if (servo_num<6){
          int serv_min = GRATSERVOMIN;
          int serv_max = GRATSERVOMAX;
          int max_degree =120;
        
        }
        else{
          int serv_min = REWSERVOMIN;
          int serv_max = REWSERVOMAX;
          int max_degree =180;
        }
        for (int degree = 10; degree<max_degree-10;degree = degree+30){
          Serial.println(degree);
        //Serial.println(pulseLen);
        pulseLen = map(degree, 0, max_degree, REWSERVOMIN, REWSERVOMAX);  
        pwm.setPWM(servo_num, 0, pulseLen);
        delay(100);
      }
      for (int degree = max_degree-10; degree>10;degree = degree-30){
        //Serial.println(pulseLen);
        pulseLen = map(degree, 0, max_degree, REWSERVOMIN, REWSERVOMAX);  
        pwm.setPWM(servo_num, 0, pulseLen);
        delay(100);
      }
      }
    }


  }
  //sCmd.readSerial();     // We don't do much, just process serial commands
} //end loop

///servo callback functions -------------------------------------------------/////////////////////////////////////////////
void gratingRoutine(int degree=90, int servoNum=0){


  pulseLen = map(degree, 0, 120, GRATSERVOMIN, GRATSERVOMAX);
  //Serial.println(pulseLen);
  pwm.setPWM(servoNum, 0, pulseLen);

}// grating routines

void pelletRoutine(int IRsensor=0,int servoNum=0, int rewardServoMovTimeLoc = rewardServoMovTime){
  int pelletDropped = 0;
  while (pelletDropped==0){
    pwm.setPWM(servoNum, 0, rewPulseLen1);
    time1=millis();
    time2=millis();
    //Serial.println(IRsensor);
    //Serial.println(rewardServoMovTimeLoc);
    while (time2-time1<rewardServoMovTimeLoc){
      IRvalue = digitalRead(IRsensor);
      //Serial.println(IRvalue);
      if(IRvalue==0){
        pelletDropped=1;
        break;
      }//if
      time2=millis();
    }// while time2-time1
    
    if (pelletDropped==0){
      pwm.setPWM(servoNum, 0, rewPulseLen2);
      time1=millis();
      time2=millis();
      while (time2-time1<rewardServoMovTimeLoc){
        IRvalue = digitalRead(IRsensor);
        //Serial.println(IRvalue);
        if(IRvalue==0){
          pelletDropped=1;
          break;
        }//if
        time2=millis();
      }//while time2-time1
    }// if   
  }//if
}// end pellet routine

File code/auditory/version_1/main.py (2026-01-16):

import numpy as np
import cv2 as cv
import pandas as pd
import supfun_sequences as sf
import time
#from serial import Serial
#import serial
import os
import csv
import sounddevice as sd
import soundfile as sf1
from tkinter import filedialog as fd
from tkinter import *
import serial

#set the default sample rate and channel for the sound card
samplerate = 192000
sd.default.samplerate = samplerate
#python -m sounddevice
sd.default.device = 3

#vol needs to be around 50dB


# Variables

# set to True for shorter time intervals to test that the sounds work fine
testing= True
#testing with longer silence in the middle of the sequence
longer_silence= False

# if this is the sort of situation where we require an arduino, either for ttls or reward delivery, set to true
microcontroller = False
arduino = None

# if the home cage is not connected, we are going to set this to true so that we will skip having the mouse enter the maze to start a new trial
no_homecage = False

# in case the homecage is connected but we still want the trials to start and end according to the "clock", set this to True
forced_timing= True

pause_between_frames = False

#set number of ROIs 
rois_number = 8

#set to true to create/modify ROIs .csv file
drawRois = False

#set to true to make individual sine sounds
make_simple_smooth_sounds = False
#set true to make individual complex sounds. This contains 2 intervals, 1 vocalisation and one pure tone
make_Simple_intervals= False

# set to true if you want to perform experiments testing the effects of temporal envelope modulation on sound preference
# w1_d1c
make_temporal_envelope_modulation = True

#w1_d2-d4
# set to true to perform experiments where the ROIS can be controls / frequencies of different AM/ intervals 
make_complex_intervals =  False
w1day2= False
w1day3= False
w1day4= False
another_day = False
#w2_d1
# set to true to make sequences of tones
make_sequences = False

#w2_d2
just_vocalisations = False

#If we are recording a video, this needs to be true and videoInput needs to be set to 0 (or 1, depending on the camera)
recordVideo = True
videoInput = 0
#"C:/Users/labadmin/Desktop/auditory_maze_experiments/maze_recordings/maze_recordings_sequences/time_2024-09-25_11_47_12mouse6705/mouse6705_time_2024-09-25_11_47_12.mp4"
#"C:/Users/aleja/OneDrive/Desktop/maze_experiments/maze_recordings/2024-08-15_16_12_305872/5872_2024-08-15_16_12_30.mp4"
#"C:/Users/aleja/Downloads/maze_test.mp4"


# setup arduino 
if microcontroller:
    try:
        # check if port is "com3" or "com5" and also in the arduino IDE, check that the baud rate is correct
        arduino = serial.Serial('COM4', 115200, timeout=0.1)
        time.sleep(2) # Wait for reboot
        print("Arduino Connected (State Machine Mode)")
    except Exception as e:
        print(f"Arduino Failed: {e}")
        arduino = None
    
# State Machine Variables
ttl_is_active = False
ttl_scheduled_off_time = 0




# Setup -- ask users for mouse info
date_time = sf.get_current_time_formatted()
date_time= f"time_{date_time}"
animal_ID, = sf.get_user_inputs()
animal_ID= f"mouse{animal_ID}"

#create new directory
base_path = os.path.join(os.path.expanduser('~'), 'Desktop/auditory_maze_experiments/maze_recordings', 'maze_recordings_sequences')
sf.ensure_directory_exists(base_path)
new_dir_path = sf.setup_directories(base_path, date_time, animal_ID)
#save recording in new directory
rec_name = f"{animal_ID}_{date_time}.mp4"
recordFile = os.path.join(new_dir_path, rec_name)
metadata = sf.collect_metadata(animal_ID)
sf.save_metadata_to_csv(metadata, new_dir_path, f"{animal_ID}_{date_time}.csv")

#define rois
entrance_rois= ["entrance1", "entrance2"]
rois_list = sf.get_rois_list(rois_number)

roiNames= entrance_rois + rois_list

#set base_name for trials list and sound array to be saved as 
base_name = f"trials_{date_time}"


#check that only one is set to true
if no_homecage and forced_timing:
    raise ValueError("Choose only one: no_homecage OR forced_timing.")


#make just sounds
if make_simple_smooth_sounds and not (make_sequences or make_Simple_intervals or make_temporal_envelope_modulation or make_complex_intervals):
    # frequency= sf.ask_music_info_simple_sounds(rois_number)
    frequency = [10000, 12000, 14000, 16000, 18735, 20957, 22543, 24065]
    # for i in range(len(frequency)):
    #     sound_data = sf.generate_sound_data(frequency[i])
    trials, sound_array = sf.create_simple_trials(rois_list, frequency)

# Make sequences of smooth sounds
elif make_sequences and not (make_simple_smooth_sounds or make_Simple_intervals or make_temporal_envelope_modulation or make_complex_intervals):

    experimental_session = "sequences"
    frequency, patterns= sf.ask_music_info_sequences(rois_number)
    path_to_vocal = "C:/Users/labuser/Downloads/vocalisationzzzzzz/trimmed_vocalisations/run3_day2-2_male_w_female_oestrus.wav"
    trials, sound_array = sf.create_trials_for_sequences(rois_list, frequency, patterns, path_to_voc= path_to_vocal)
    #make all arrays the same size because otherwise it won't save sound arrays
    min_length = min(len(arr) for arr in sound_array)
    # Trim each array to the minimum length
    trimmed_sound_arrays = [arr[:min_length] for arr in sound_array]


#make complex sounds
elif make_Simple_intervals and not (make_sequences or make_simple_smooth_sounds or make_temporal_envelope_modulation or make_complex_intervals):
    #essentially this gives me the option to be prompted what I want as intervals vs hard coding them
    manual = False
    if manual:
        frequency, intervals, intervals_names = sf.ask_info_intervals(rois_number)
    else: 
        tonal_centre = 10000 #Hz
        intervals_list = ["perf_5", "perf_4", "maj_6", "tritone", "min_2", "maj_7"]
        frequency, intervals, intervals_names = sf.info_intervals_hc(rois_number, tonal_centre, intervals_list)

    trials, sound_array = sf.create_trials_for_intervals(rois_list, frequency, intervals, intervals_names)
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

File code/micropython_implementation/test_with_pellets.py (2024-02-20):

from machine import Pin
import machine
import servo
import pca9685
import time



detector_food1=Pin(15,Pin.IN)

scl=Pin(25)
sda=Pin(26)
 

# i2c = I2C(1,scl=Pin(26),sda=Pin(25))
i2c=machine.SoftI2C(scl=scl,sda=sda)
# addresses = i2c.scan()
# print(addresses)
address = i2c.scan()
print(address)
address = address[0]

time.sleep_ms(10)
#pca= pca9685.PCA9685(i2c=i2c,address=address)
#pca.freq=50

motorReward1=0




restAngle = 45
horizontalAngle = 90
verticalAngle = -180

    #pca.pwm()
    #pca.duty(i,100)
ser=servo.Servos(i2c=i2c)

#ser.position(3,duty=4096)

numTrials = 10
#Gratings move to rest at start of trial
for trial in range(1,numTrials+1):
    print("trial "+str(trial))
    giveReward=True
    
    while giveReward:
        ser.position(motorReward1,degrees=30)
        time1 = time.ticks_ms()
        time2 = time.ticks_ms()
        while time2-time1<300:
            #print("here")
            notDropped = detector_food1.value()
            #print(notDropped)
            time2 = time.ticks_ms()
            #print(time2-time1)
            if not notDropped:
                print("detected")
                giveReward=False
                break
                
        ser.position(motorReward1,degrees=60)
        time1 = time.ticks_ms()
        time2 = time.ticks_ms()
        while time2-time1<200:
            notDropped = detector_food1.value()
            #print(notDropped)
            time2 = time.ticks_ms()
            if not notDropped:
                print("detected2")
                giveReward=False
                break
        
        time.sleep_ms(500) 

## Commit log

2022-06-25 start 3D designs
    [gratings.scad, spout_holder.scad]
2022-06-27 update gratings
    [gratings.scad, gratings.stl]
2022-07-25 adjust plates thickness
    [gratings.scad, gratings.stl]
2022-09-07 few 3d models for the maze
    [habituation_sink.3mf, habituation_sink.stl, moveable_wall.3mf, moveable_wall.stl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]
2022-09-15 work on enclosure for first prototype
    [enclosure.FCStd]
2022-09-15 update main enclosure
    [enclosure.FCStd]
2022-09-15 restructure folders/files
    [enclosure.FCStd, gratings.scad, gratings.stl, habituation_sink.3mf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]
2022-09-20 first version of enclosure
    [enclosure.FCStd]
2022-09-20 upload enclosure production files
2022-09-20 update enclosure
    [enclosure.FCStd]
2022-09-22 origninals of the 3d models (shapr3d)
    [spout_holder.scad, transfer_tunnel.stl]
2022-10-05 add camera holder model
    [syringe_holder.scad]
2022-10-07 add small example for infrared sensor
2022-10-24 first prototype spout holder
    [spout_holder-holder_left.amf, spout_holder-holder_right.amf, spout_holder-main_plate.amf]
2022-10-24 create freecad version of transfer tunnel
    [transfer_tunnel-Cut.amf, transfer_tunnel.FCStd, transfer_tunnel.stl]
2022-12-15 solid reward models
    [cog.stl, funnel.stl, servo_tray.stl, slider_old.stl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]
2023-01-05 update code and 3d designs
    [spout_holder-holder_left.amf, spout_holder-holder_right.amf, spout_holder-main_plate.amf]
2023-03-03 solved bug with I2C board
2023-03-24 start bonsai implement
    [trials.csv]
2023-06-28 update the bonsai code, now only entering moments are being detected
    [trials.csv, trials_2columns.csv]
2023-07-03 somewhat working solution for counting trials and setting motors
    [trials_2columns.csv]
2023-07-06 organise repo a bit, update code with minimal example and update csv file
    [trials_2columns.csv]
2023-08-04 update others code
    [angle_tunning.csv, food_tunning.csv]
2023-08-14 latest version of code
    [motor1.csv, motor2.csv, motor3_grid1.csv]
2023-08-14 update version
    [motor1.csv, trials_2columns.csv]
2023-08-25 more test
    [rewards.csv, trials_2columns.csv]
2023-09-08 first working version of the maze I suspect
    [trials_2columns - Copy - Copy.csv]
2023-10-16 add first code on the python version of the maze
    [rois.csv, trials_2columns.csv]
2023-10-24 Add files via upload
    mice_loc has a a column for each ROI and it tells you +1 or -1 if the mouse was present in it or not. There is one row per frame.
2023-10-24 Add files via upload
    commented version.
    data in "mice_loc". columns are ROIs and rows the time. there is one row per frame (60fps)
    - ROIs are still set
2023-10-25 Add files via upload
    This opens up the camera and allows you to select the ROIs you want. when finished you press 'q'. the Reward areas are saved as reward_pts. which can be used with the next script for costumised rewar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
2023-10-25 Add files via upload
    select the reward points on your camera to later use on the main code
2023-11-13 Cleaning up 3D designs
    Moved previous versions into the archive folder
    [new_wall_maze.FCStd, new_wall_maze_cog_v4.stl, new_wall_maze_cog_v6.FCStd, new_wall_maze_cog_v6.stl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]
2023-11-15 reorganize 3D parts folders
    [enclosure.FCStd, gratings.scad, gratings.stl, habituation_sink.3mf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]
2023-11-15 create flexible control system for motors using arduino
2023-11-16 Final movable wall model
    [new_wall_maze_v9.FCStd, new_wall_maze_v9.stl]
2023-11-24 update code
    [rois.csv, trials_2columns.csv]
2023-11-29 add camera box scad file
    [cam_box.scad]
2023-11-30 Final Version of 3D parts
    new Movable wall v 10
    new reward chute wall
    [new_wall_maze_v9.FCStd]
2023-12-04 organising files
    [moveable_wall.3mf, moveable_wall.stl, new_wall_maze.FCStd, new_wall_maze_cog_v4.stl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]
2023-12-04 some more code updates
    [rois1.csv]
2023-12-05 sequence rules example csv
    I have uploaded an example csv of how the sequence rules can be read.
    [reward sequences .xlsx]
2023-12-14 Reward Chute Wall
    Uploaded the final version of the reward wall chute.
    [reward_chute_Wall.3mf, reward_chute_Wall.FCStd, reward_chute_Wall.stl, reward_chute_Wall_v3.3mf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]
2024-01-16 archived old files from 3Dmodels
    archived the following 3D files from 3Dmodels
    solid_reward_tray
    spout_holder
    syringe_holder
    [cog.stl, funnel.stl, servo_tray.stl, slider_old.stl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]
2024-01-24 add first code making the servo and pellet detector loop
2024-02-13 add code for arduino and for generating trials
    [grating_maps.csv, large.csv, reward sequences .xlsx, reward_sequences.csv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]
2024-02-14 clean arduino code
2024-02-14 more work on main code
    [grating_maps.csv, reward_sequences.csv, rois1.csv, trials.csv]
2024-02-14 updated 3d models
    Archived Shapr3d models of maze cover and replaced them with FreedCad models
    Uploaded version 1 of electronics enclosure
    [electronics_enclosure.FCStd, maze_cover_A_v2.FCStd, maze_cover_A_v2.stl, maze_cover_B_v2.FCStd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]
2024-02-17 update code to deal with cases where a wrong location leads to no reward
    [trials.csv]
2024-02-19 updated Maze cover designs
    Archived v2 of maze cover and uploaded v3.
    [maze_cover_A_v2.FCStd, maze_cover_A_v2.stl, maze_cover_A_v3.FCStd, maze_cover_A_v3.stl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]
2024-02-20 fix code merge and start testing
    [trials.csv]
2024-02-20 finsih merge, streamline testing, clean some bugs and repository
    [10_2024-02-20_16_40_49.csv, large.csv, reward_sequences_old.csv, reward_sequences_old.xlsx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]
2024-02-26 camera box v2
    uploaded new version of camera box/holder and archived the old one.
    [cam_box.scad, camera_box_v2.FCStd, camera_box_v2.stl]
2024-02-27 camera box v3
    new version of camera box uploaded
    [camera_box_v3.FCStd, camera_box_v3.stl]
2024-02-27 update arduino code, add test routine
    [camera_box_v2.FCStd]
2024-02-27 update arduino code
2024-03-04 found problem in food dispenser to be the rating of the resistors connected to the IR leds
2024-03-05 Electronics enclosure v2
    uploaded updated version of electronics enclosure and archived old one.
    [electronics_enclosure.FCStd, electronics_enclosure_bottom_v2.stl, electronics_enclosure_lid_v2.stl, electronics_enclosure_v2.FCStd]
2024-03-05 electronics enclosure
    uploading correct versions
    [electronics_enclosure_lid_v2.stl, electronics_enclosure_v2.FCStd]
2024-03-21 camera lid stl
    [camera_lid_v1.stl]
2024-04-26 updated codes for frame background subtraction
2024-05-08 clean up folder structer adn add data from session recording, reimplement how trials are calculated
    [angle_tunning.csv, food_tunning.csv, motor1.csv, motor2.csv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]
2024-05-09 data stored on a trial by trial basis
    [auditory_rois.csv, test.csv, test1.csv]
2024-05-10 fix problem with session stage and experiment phase, and fix bugs with file location
2024-05-10 working version of Ale's auditory task
    [grating_maps.csv, reward_sequences.csv]
2024-05-13 add a print statedment to debug the reward system
2024-05-13 update simplercode with the current version of the code and add serial flush to grating motors
2024-05-13 clean up repo
    [10_2024-02-20_16_40_49.csv, test.csv, trials.csv]
2024-05-15 start readme for the code with instructions to set it up, and make sure all motors stay in zero position for habituation phase
2024-06-17 add requirements.txt, update some of the main code and supfun
    [grating_maps.csv]
2024-07-11 update arduino code, so that it is fine tuned to the grating motors
2024-07-19 code to take care of servo of calibration
2024-07-26 change arduino code for testing of an arduino uno instead of the ESP32
2024-07-29 update auditory
    [trials_2024-07-29_14_25_27.csv]
2024-07-29 first working version of auditory task
    [trials_2024-07-29_14_25_27.csv]
2025-01-20 new version of 3d parts
    uploading modified versions of the stimulus presentation wall (ephys maze) and the maze cover (8-arm maze) for maze 2.0
    [maze_cover_B_v4.FCStd, maze_cover_B_v4.stl, new_wall_maze_v11.FCStd, new_wall_maze_v11.stl]
2025-02-12 Add files via upload
    Maze entrance for a maze with walls 5 cm wide, 10 cm high
    [Maze2_transfer_tunnel_higher.walls.3mf]
2025-05-12 updating 3d models
    [new_wall_maze_v13.FCStd, new_wall_maze_v14.FCStd, new_wall_maze_v15.FCStd, reward_chute_Wall_v4.3mf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]
2025-05-15 add changes so that the system controls 4 more motors
    [grating_maps.csv]
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2025-05-20 Update and rename code/auditory/frequency_response_speaker.csv to code/auditory/speaker calibration scripts/frequency_response_speaker.csv
    [frequency_response_speaker.csv]
2025-06-11 adding usv_analysis
    [angle_tunning.csv, auditory_rois.csv, food_tunning.csv, motor1.csv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]
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2025-12-11 stuff worked (it was version 3!!)
    [trial_000_data.csv, trial_001_data.csv, trial_002_data.csv, trial_003_data.csv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]
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2026-01-20 modified analysis code
    [maze_boundary.csv, trial_000_data.csv, trial_001_data.csv, trial_002_data.csv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]
2026-02-05 updated supfun and analysis code
    [maze_boundary.csv]
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
